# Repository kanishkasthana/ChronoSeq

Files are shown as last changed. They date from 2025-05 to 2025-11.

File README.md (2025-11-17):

# Software and Protocols for [ChronoSeq](https://github.com/kanishkasthana/ChronoSeq)

### [Project Map](https://kanishkasthana.github.io/ChronoSeq/sitemap.html)
+ First time users should visit [this website](https://kanishkasthana.github.io/ChronoSeq/sitemap.html) first as it provides an overview of the ChronoSeq project. You can click on and directly go the the relevant information. There are two main notebooks for Device assembly and Device operation as linked below. These notebooks should have the links to help you follow the correct instructions in the right order. Please read the disclaimer below before starting. 

### Getting Started with Software 
+ Install [Git X86-64-Bit for Windows](https://git-scm.com/download/win) and [Anaconda X86-64-Bit for Windows](https://www.anaconda.com/download), on your [Windows X86-64 Bit PC](Computer%20Selection.md).
+ Type "Git Bash" in the Search bar next to the Start Button. Using Git Bash clone this repository.
    + Using Git Bash [Navigate to the directory](https://tutorials.codebar.io/command-line/introduction/tutorial.html) where you want to store this repository.
    + This repository has submodules. In Git Bash, use the command ```> git clone --recursive https://github.com/kanishkasthana/ChronoSeq.git```  when cloning this repository so the submodules are also cloned.
+ Type "Anaconda Prompt" in the Search bar next to the Start Button. Now create a [new environment](https://conda.io/projects/conda/en/latest/user-guide/tasks/manage-environments.html#creating-an-environment-from-an-environment-yml-file) called Chrono from [this file](conda_environment_file/chrono.env.yml)
+ [Activate the Environment](https://docs.conda.io/projects/conda/en/latest/user-guide/tasks/manage-environments.html#activating-an-environment) from the Anaconda Prompt. 
+ Using the Anaconda Prompt navigate to the directory for the git repository you cloned.
    + Alternatively you can modify your Anaconda Prompt shortcut so that it always activates the Chrono Environment and launches at the location of your Git repository. I've included [an example here](conda_environment_file/Anaconda%20Prompt.lnk).
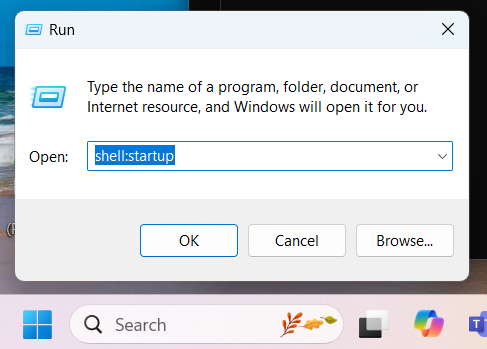
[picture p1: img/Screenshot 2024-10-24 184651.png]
    + Open Run and type ```shell:startup``` to open your startup folder.<br>
    + You can copy the shortcut included to this startup folder.
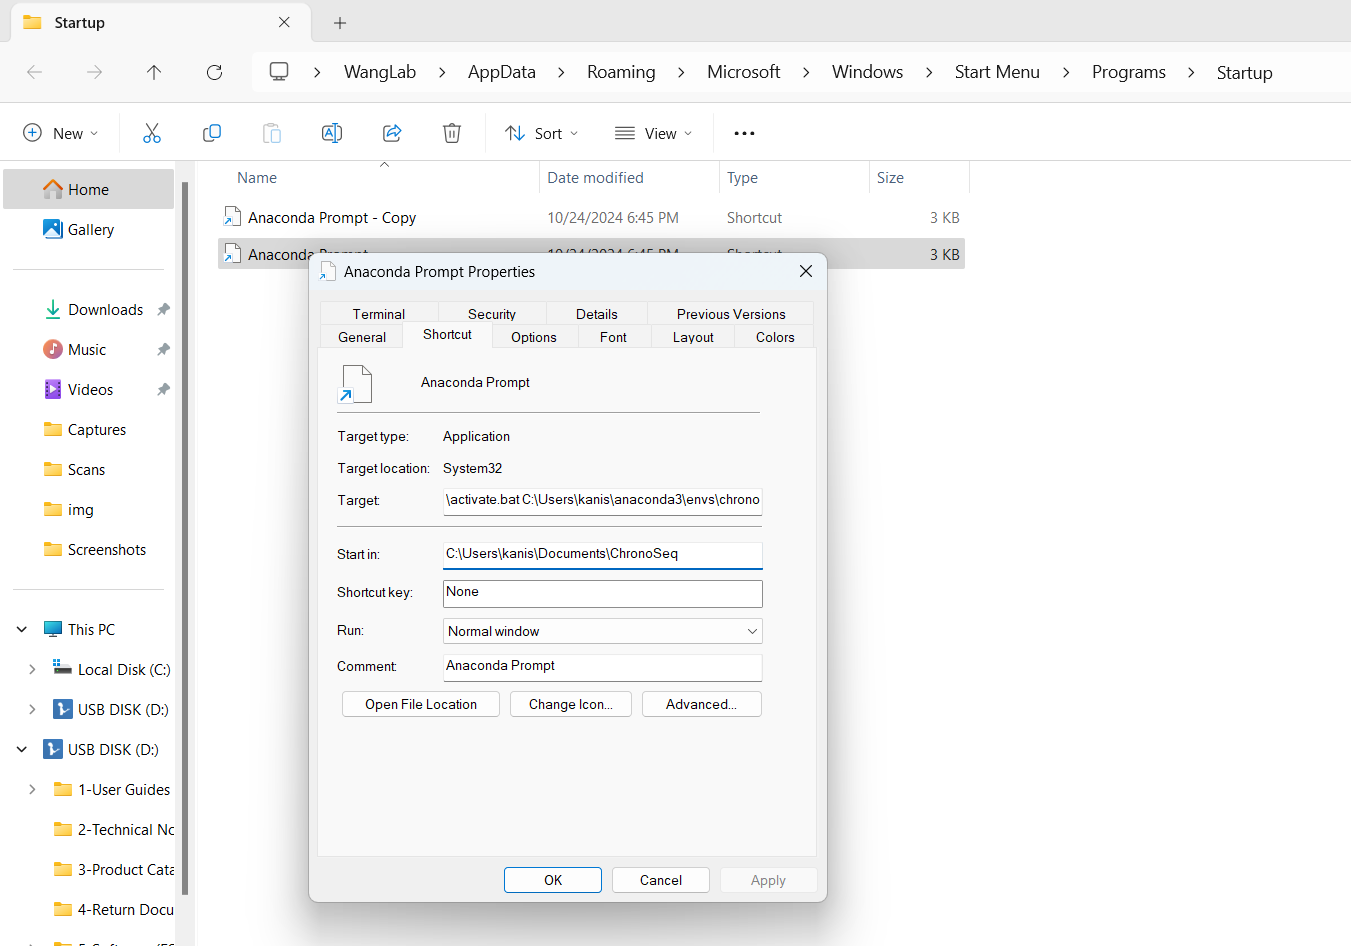
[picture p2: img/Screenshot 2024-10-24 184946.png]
    + Then right click the shortcut and change the ```Target``` and ```Start In``` sections so that a command line terminal with the environment automatically activated opens during startup.<br>
+ Using Anaconda Prompt Run ```> jupyter notebook``` 
+ The links to the notebooks below are intended to be opened using Jupyter. Click the image below to watch a video of the process.
<br>[](https://www.youtube.com/watch?v=qbhCONpUdx0)

### Device Assembly
+ See the [Device Assembly and Setup notebook](instructions_for_device_assembly_and_setup.ipynb) for a detailed description of how to set everything up.

### Storage of Dropseq beads upon receipt
+ You should receive your beads suspended in Ethanol.
+ Store these beads in a new box at -20&deg;C before you start your experiments or for long term storage. Label the box with the Date you received the beads, the bead type and the batch number.

### Running the Device and Preparation for Experiment
+ Once you are ready, see [this notebook](protocol_and_software_for_running_chronoseq_device.ipynb#Protocol-for-Preparation-and-Operation-of-the-ChronoSeq-Device-for-an-Experiment.) on how to run the Device and the preparation needed.

### Videos of Device Operation
+ Click the image below to watch a video of the view from inside the microfluidic chip during an Injection.<br>[](https://www.youtube.com/watch?v=J2O1kA4chU0)
+ Click the image below to watch an outside view of the ChronoSeq device during an Injection. <br>[](https://www.youtube.com/watch?v=qFouf2HrKSk)

### Build Compilation Music Video
+ Click the image below to watch a music video of the iteration/build process for making the ChronoSeq device.<br>[](https://www.youtube.com/watch?v=QpMUR4AgpgA)

# License

We have released this work under a [CC BY-NC-SA 4.0 License](LICENSE).

# Disclaimer

Dear Fellow Users and Researchers,
<br><br>
We are thrilled that you are interested in assembling the ChronoSeq Device we have created. However, it is important to note that we cannot be held responsible for any injuries that may occur during the assembly and operation process.<br>
While we strive to provide clear and concise instructions, the assembly of this open source hardware requires a certain level of skill and experience. Therefore, we strongly recommend that you take all necessary precautions to ensure your safety.<br>
Please read and follow all instructions carefully, and make sure that you have the necessary tools and protective equipment. If you are unsure about any step or procedure, do not hesitate to seek the advice of a qualified professional. You are also welcome to raise [an issue](https://github.com/kanishkasthana/ChronoSeq/issues) or [start a discussion](https://github.com/kanishkasthana/ChronoSeq/discussions) if you have any questions or if anything is unclear.<br> 
<br>
By using or constructing this open source hardware design, you acknowledge and agree to the following:
1. Liability Waiver: The creators, designers, and contributors of this open source hardware project cannot be held liable for any injuries, damages, or losses resulting from the use, construction, or modification of this hardware.
2. Assumption of Risk: You, as the builder or user, assume all risks associated with the construction, use, and modification of this hardware. This includes, but is not limited to, personal injury, property damage, or any other potential harm.
3. Waiver of Legal Action: By proceeding with the use or construction of this open source hardware, you waive your right to sue, hold legally responsible, or seek compensation from the creators, designers, or contributors for any reason related to this project.
4. No Warranty: This open source hardware is provided "as is" without any express or implied warranties. The creators make no guarantees regarding its safety, functionality, or fitness for any particular purpose.
5. Responsibility: You are solely responsible for ensuring that you follow all safety precautions, local laws, and regulations when building or using this hardware.
6. Modifications: Any modifications you make to the original design are your sole responsibility, and the original creators bear no liability for the results of such modifications.
<br>By proceeding with the use or construction of this open source hardware, you indicate your understanding and acceptance of these terms.

Thank you for choosing our open source hardware, and we hope that you enjoy the building and operation process.
<br><br>
Best regards,
<br>ChronoSeq Team:
<br>Kanishk Asthana [kasthana@ucsd.edu](mailto:kasthana@ucsd.edu) , [X/Twitter](https://x.com/kanishk_asthana)
<br>Alexander Jambor [ajambor@ucsd.edu](mailto:ajambor@ucsd.edu)
<br>Wei Wang [wei-wang@ucsd.edu](mailto:wei-wang@ucsd.edu)

# Data Processing and Analysis

+ Check out the [ChronoSeq-Tools repo](https://github.com/kanishkasthana/ChronoSeq-Tools) to help process your raw data.
+ Check out the [ChronoSeq-QC repo](https://github.com/kanishkasthana/ChronoSeq-QC) to see how the QC plots were generated.
+ Check out the [ChronoPack repo](https://github.com/anjambor/ChronoPack) to see how the ChronoSeq data was analysed.

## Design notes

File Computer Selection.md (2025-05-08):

### We purchased the [Dell Inspiron Small Desktop](https://www.dell.com/en-us/shop/desktop-computers/inspiron-small-desktop/spd/inspiron-3030-small-desktop/useishbts3030gssh). 
+ Please purchase a Computer with the same Tech Specs or better.
+ Make sure there are at least four USB 3.2 Gen 1 Ports on your machine.
+ We used an [adapter to convert one of the USB 3.2 Gen 1 Type C ports to a Type A port](https://www.amazon.com/dp/B0CNK3YK1J).
+ The price was 600 USD before taxes and shipping in October 2024.

### Tech Specs:

+ Processor:
    + Intel® Core™ i5 14400 (20 MB cache, 10 Cores, 16 threads, up to 4.7 GHz)
+ Operating System
    + Windows 11 Home, English, French, Spanish
+ Graphics Card
    + Intel® UHD Graphics 730
+ Memory 
    + 16GB DDR5, 1x16GB, at 4400 MT/s
+ Storage
    + 512GB M.2 PCIe NVMe Solid State Drive
+ Ports
    + Front:
        + 2 USB 2.0 Type-A ports
        + 1 USB 3.2 Type-A Gen 1 port
        + 1 USB 3.2 Type-C Gen 1 port
        + 1 Universal headset jack
    + Rear:
        + 2 USB 2.0 Type-A ports with Power on/Wake support
        + 2 USB 3.2 Type-A Gen 1 port
        + 1 Audio line-out port
        + 1 DisplayPort 1.4 port
        + 1 RJ-45 Ethernet port
        + 1 HDMI 1.4b port <br> Note: The maximum resolution supported by HDMI 1.4b port is 1920 x 1200.
+ Dimensions
    + Height (rear): 11.42 in. (290.00 mm)
    + Height (front): 11.42 in. (290.00 mm)
    + Width: 3.65 in. (92.60 mm)
    + Depth: 11.53 in. (292.80 mm)
+ Wireless 
    + Realtek Wi-Fi 6 RTL8852BE, 2x2, 802.11ax, MU-MIMO, Bluetooth® wireless card

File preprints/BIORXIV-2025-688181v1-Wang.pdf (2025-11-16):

Minute-scale single-cell transcriptomics enables dynamic modeling of cellular behavior

Kanishk Asthana†‡,1,2, Alexander N. Jambor†,1,2, and Wei Wang‡,1,2,3,4

1 Department of Chemistry and Biochemistry, University of California San Diego, La Jolla, CA 92093, USA
2 Bioinformatics and Systems Biology PhD Program, University of California San Diego, La Jolla, CA 92093, USA 3 Department of Cellular and Molecular Medicine, University of California San Diego, La Jolla, CA 92093, USA
4 Lead contact
† Equal contribution
‡ Corresponding authors

Corresponding author contact information: Kanishk Asthana: kasthana@ucsd.edu Wei Wang: wei-wang@ucsd.edu

Abstract

Dynamic cellular processes such as signaling, fate decisions, and intercellular communication unfold on minute timescales, a regime inaccessible to conventional transcriptomic methods. This temporal gap has fundamentally limited the development of predictive, causal models of cell behavior. Here, we bridge this gap by introducing ChronoSeq, an automated single-cell RNA sequencing platform that achieves genome-wide profiling with a temporal resolution as brief as seven minutes. By integrating automated live-cell sampling with molecular time-barcoding, ChronoSeq captures rapid transcriptional dynamics with high fidelity. Applying ChronoSeq to TNF-α stimulated cells, we discovered a rapid, heterogeneity-driven bifurcation in the NF-κB response that was previously unobservable. We further demonstrate that the highdensity temporal data generated by ChronoSeq enables a new class of computational models that dramatically outperform existing methods in inferring the directionality and targets of post-translationally regulated transcription factors. Finally, in a multicellular co-culture, ChronoSeq resolved a paracrine signaling cascade in real time, identifying both the timing and molecular identity of the intercellular relay. By providing a framework to measure dynamics, infer regulation, and model communication at the true pace of biology, ChronoSeq establishes a new foundation for dynamic systems biology.

Introduction
Building predictive, dynamic models of cellular behavior, the vision of a “Virtual Cell”¹,2, requires experimental data that reveal how gene regulation and cell-cell communication unfold in real time. Achieving this vision depends on three core capabilities: capturing transcriptional dynamics on the natural timescales of signaling and fate decisions, inferring causal rather than correlative gene regulatory networks (GRNs), and resolving the timing of multicellular communication that coordinates collective responses. Yet current methodological and data limitations have kept these goals largely out of reach.

Many cellular processes operate on minute timescales³⁻⁵
, a regime inaccessible to standard single-cell RNA sequencing (scRNAseq)⁶⁻¹⁶ . For example, the NF-κB signaling cascade activates transcriptional responses within 5 minutes of TNF-α stimulation and peaks at around 25 minutes¹⁷, timescales that are effectively invisible at the 30–60 minute resolution of existing scRNA-seq. Without dense, accurately timed expression measurements, computational efforts to infer causality or simulate cellular decision-making remain fundamentally constrained.

Several specialized methods have attempted to address this gap, but each fall short of combining fidelity, temporal resolution, and throughput. Metabolic labeling¹⁸⁻²³ and scGROseq²⁴ can detect nascent transcripts yet suffer from manual processing errors and low scalability. Liveseq⁶ preserves cell viability but has hourly sampling intervals and limited throughput. Live-cell imaging²⁵⁻²⁷ captures real-time trajectories only for a few marker genes and is hindered by phototoxicity and narrow genomic coverage²⁸. No current technology achieves genome-wide, minute-scale measurements under physiological conditions with full experimental automation, capabilities that are essential for generating the benchmark datasets required for dynamic in silico modeling.

To bridge this gap, we introduce ChronoSeq, an automated droplet-based single-cell RNA sequencing platform that performs genome-wide profiling with a sampling interval as brief as seven minutes. ChronoSeq integrates automated sampling with molecular time-barcoding into a single workflow, preserving cell health while capturing transcriptional dynamics over extended perturbations. Together with a companion computational suite, ChronoPack, this technology provides an integrated framework to measure dynamics, infer causality, and model intercellular communication, the core components of Virtual Cell.

We demonstrate these capabilities through proof-of-concept studies addressing rapid signaling, causal inference, and multicellular communication. Minute-scale profiling of TNF-α stimulated K562 cells revealed a rapid bifurcation into erythroid and non-erythroid trajectories, directly capturing fate transitions as they occurred. Using ChronoPack, we reconstructed temporally informed GRNs that outperformed existing inference methods, yielding mechanistic insight into early transcriptional regulation. Finally, in a co-culture of THP1 macrophages and K562 cells, ChronoSeq resolved secondary paracrine signaling induced by the LPS stimulation of THP1 cells, pinpointing the timing and molecular identity of secreted factors mediating cross-cell activation.

By combining genome-wide, minute-scale temporal profiling with causal network inference and intercellular dynamics, ChronoSeq establishes a new foundation for dynamic systems biology. This integration brings the Virtual Cell concept within reach, linking molecular mechanism to phenotype in predictive, quantitative terms.

Results
An automated platform for minute-scale temporal scRNA-seq
To directly observe rapid transcriptional dynamics, we developed ChronoSeq, an automated platform that integrates live-cell culture with droplet-based scRNA-seq. The system performs programmed sampling at intervals as short as seven minutes, co-encapsulating each cell with uniquely barcoded Time-Tag beads (Fig. 1a, Fig. S2, Supplementary Movie 1). Immediate lysis upon droplet formation preserves the transcriptional state, while all timepoints are processed within a single library to dramatically reduce labor while eliminating batch effects and manual variability (Fig. S1). Continuous cell maintenance under physiological conditions ensures that captured profiles reflect authentic biological responses.

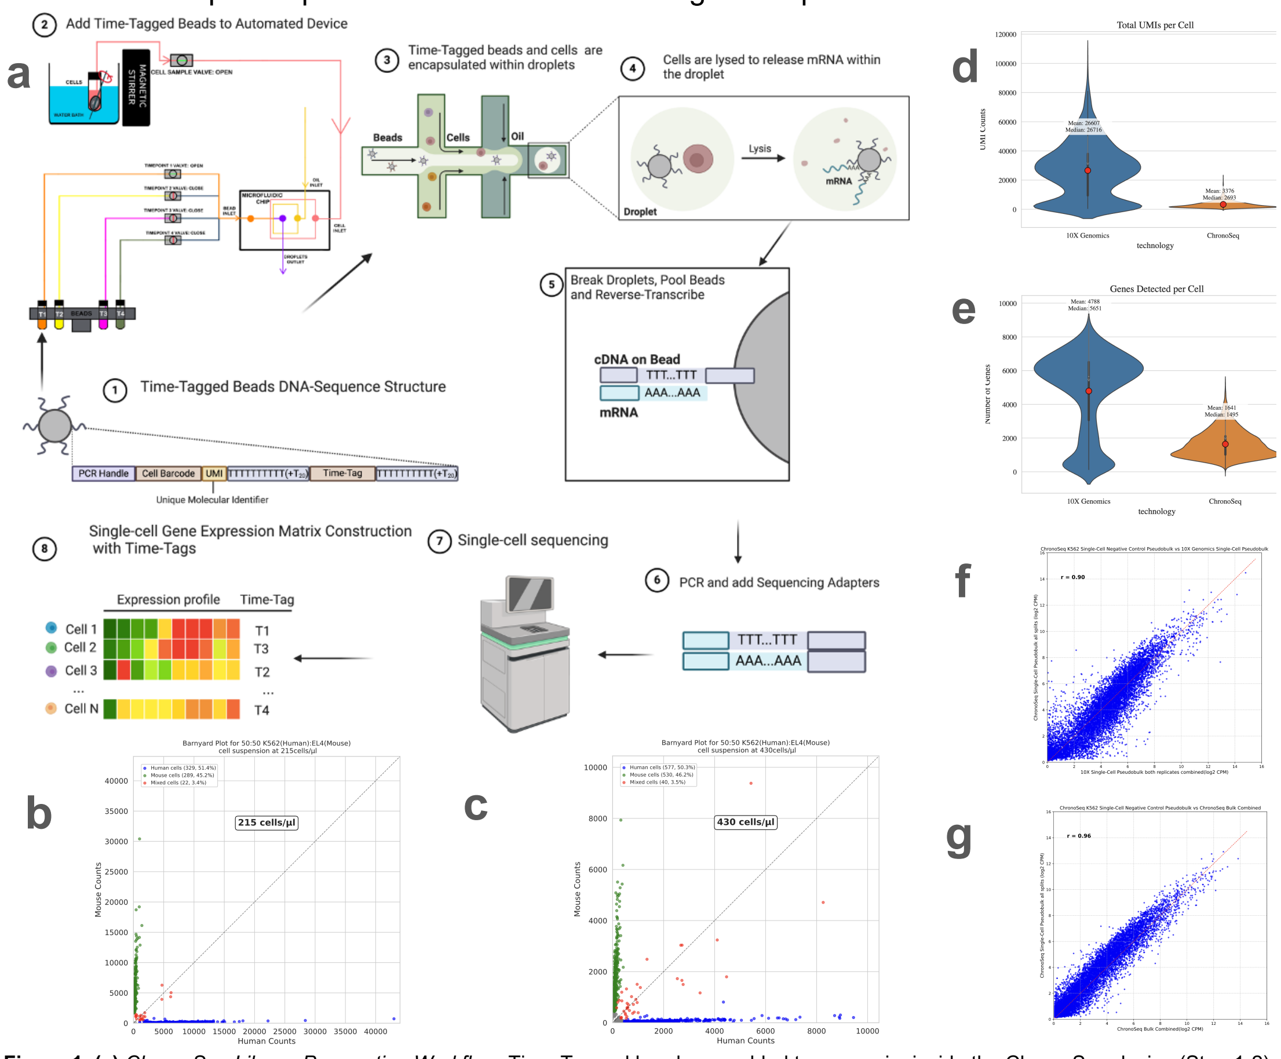
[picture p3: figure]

Figure 1. (a) ChronoSeq Library Preparation Workflow: Time-Tagged beads are added to reservoirs inside the ChronoSeq device (Step 1-2). Our current system supports 12 unique Time-Tags, each Time-Tag is added to its own dedicated reservoir. Cells suspended in a culture media are loaded into another reservoir maintained at 37°C and 5%CO2. The ChronoSeq device then automatically co-injects Time-Tags 1-12 with samples 1-12 from the Cell reservoir into a microfluidic chip at programmed time intervals of 7 minutes or longer (Supplementary Movie 1 and Figure S2). This results in droplets where cells collected from each sample 1-12 are present with ChronoSeq beads with the same Time-Tags 1-12 (Step 3). Cells are immediately lysed upon droplet formation and kept on ice to preserve the transcriptome until all 12 samples are collected (Step 4). For samples with high RNAase activity, RNAase inhibitor is added to each sample to help further maintain RNA integrity. Next, following the same process as Drop-seq, droplets are broken, pooled, and reverse transcribed together in unified library preparation workflow for all samples. The cDNA on the beads is amplified and sequencing adapters are added (Steps 5-6). The library is sequenced and processed with our ChronoSeq-Tools pipeline to create Digital Gene Express Matrices (DGEs) with a Time-Tag number for each cell (Steps 7-8). (b,c) Species-mixing barnyard plots for 50:50 K562(Human) and EL4(Mouse) cells at two commonly used ChronoSeq working concentrations (215 cells/ul and 430 cells/ul). (d-g) We generated K562 negative control datasets using both single-cell and bulk sampling using the ChronoSeq device. For both bulk and single-cell datasets, K562 cells were maintained inside the ChronoSeq device and samples were taken using the ChronoSeq device at programmed intervals of 10 minutes. For the bulk dataset, cells sampled by the device

We manufactured (Fig. S3) and validated the fidelity of the 12-plex Time-Tag barcode system using mixed human–mouse samples. Each tag cleanly partitioned species-specific transcripts, with minimal barcode cross-talk (<=1.6% mixed beads per tag; Fig. S4). Automated sampling within the ChronoSeq device showed similarly precise tagging and each cell population was exclusively labeled with its designated barcode (Fig. S5). ChronoSeq’s single-cell capture efficiency matched commercial standards, with a doublet rate below 4% across operational cell concentrations (Fig. 1b,c). We captured an average of 636 cells per Time-Tag. Together, these results demonstrate that ChronoSeq achieves fully automated, high-integrity sample tagging and single-cell encapsulation.

To benchmark transcriptional accuracy independently of temporal resolution, we profiled unstimulated K562 cells using ChronoSeq. Despite the number of detected genes and transcripts per cell being lower than 10X Chromium (Fig. 1d,e), ChronoSeq exhibited quantitative fidelity: pseudobulk profiles from ChronoSeq single cells correlated nearly perfectly with ChronoSeq bulk RNA-seq (r = 0.96) and strongly with 10x Chromium pseudobulks (r =
0.90) (Fig. 1f,g). These results confirm that ChronoSeq accurately preserves transcriptional signatures, with minimal bias introduced by automated sampling. The high concordance establishes a robust foundation for interpreting minute-scale biological dynamics.

ChronoSeq reveals rapid fate bifurcation during the NF-κB inflammatory response
To demonstrate ChronoSeq’s ability to resolve rapid transcriptional dynamics, we profiled K562 cells responding to TNF-α stimulation at 10-minute intervals over 2 hours, which is known to activate the NF-κB pathway. Temporal pseudobulk profiles showed high concordance with matched qPCR timecourses for representative NF-κB target genes (Fig. S6), validating ChronoSeq’s ability to capture real-time dynamics.

We developed ChronoPack, an open-source computational suite for quantitative analysis of time-resolved single-cell data (Fig. 2a). The suite integrates standard preprocessing, expression correction, and metacell construction, followed by trajectory inference using WaddingtonOT³⁰ to derive a probabilistic cell-state transition kernel across time. This kernel enables cell-fate mapping, dynamic clustering, and the identification of early predictive genes. Temporal gene expression is modeled with negative-binomial generalized additive models (NB-GAMs) using tradeSeq³¹ to detect statistically significant expression trends. Building on these results, ChronoPack can also infer causal gene regulatory networks from time-resolved dynamics and reconstruct paracrine signaling by integrating ligand–receptor databases with Granger causality analysis. Collectively, ChronoPack provides a unified framework for inferring causal regulation and intercellular communication from high-temporal-resolution scRNA-seq data.

Trajectory reconstruction using ChronoPack revealed a striking, previously uncharacterized bifurcation in the NF-κB response emerging within minutes of stimulation (Fig. 2a,e). One subpopulation activates the classical inflammatory program, marked by strong induction of NF-κB hallmark genes like NFKBIA and ICAM1, whereas a smaller, erythroid-like subpopulation responds weakly (Fig. 2c,d). This rapid divergence indicates that intrinsic cell-state

were manually mixed with Time-Tags 1-12. d-e) We downloaded both replicates of a published K562 dataset²⁹ generated using the commercially available 10X Genomics Chromium 3’ single-cell RNA-seq technology for comparison: (d) shows a violin plot comparing mean and median transcripts captured, (e) shows a violin plot comparing genes detected for the 10X Genomics dataset and ChronoSeq single-cell K562 negative control dataset. (f-g) We prepared pseudobulks across all Time-Tags for both bulk and single-cell ChronoSeq K562 negative control datasets. We also prepared a combined pseudobulk for both 10X Genomics K562 replicates. (f) shows a correlation scatterplot between the 10X Genomics and ChronoSeq single-cell K562 pseudobulks. ChronoSeq shows a high concordance with 10X Genomics with a correlation coefficient r=0.90. (g) Comparison of ChronoSeq single-cell and bulk shows even higher concordance with a correlation coefficient r=0.96.

heterogeneity preconfigures responsiveness to inflammatory signaling, influencing both the timing and magnitude of NF-κB activation.

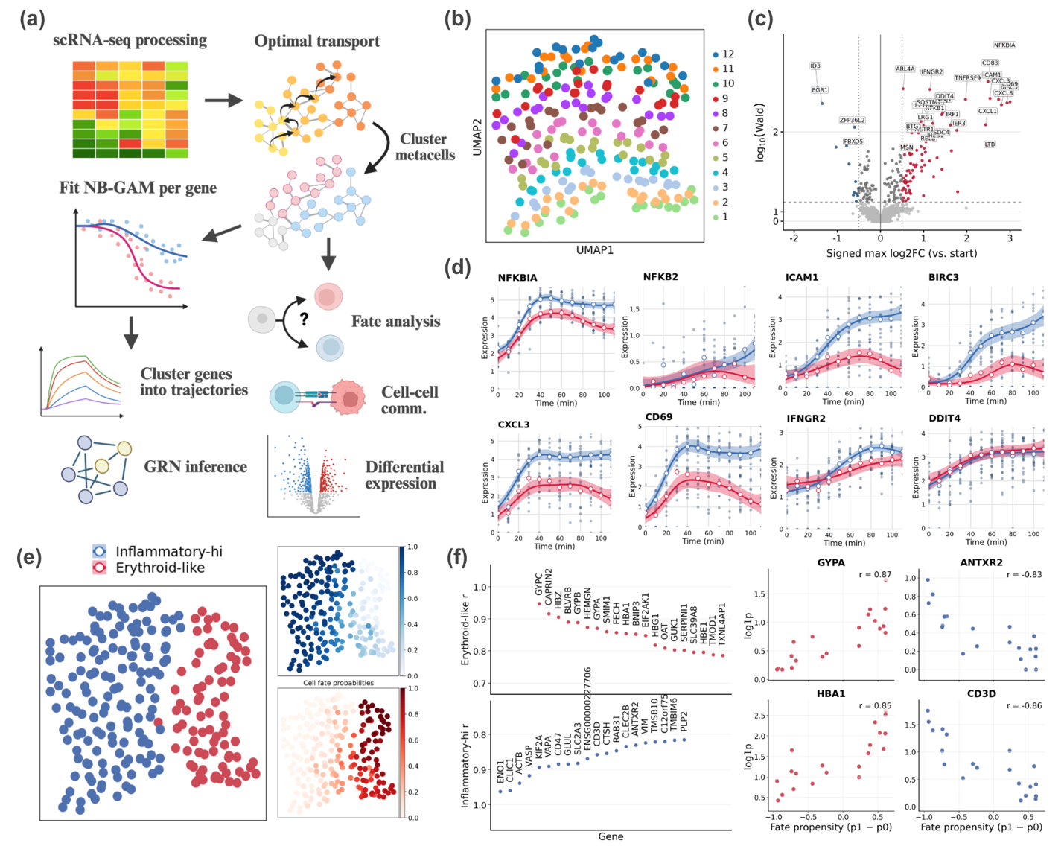
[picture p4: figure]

We next quantified gene-specific dynamics along each trajectory using negative-binomial generalized additive models (NB-GAMs). After filtering for genes with Time-Tag-specific capture biases, we identified 184 high-confidence temporally regulated genes, including both upregulated and a few immediate-early genes like ID3 and EGR1 which decreased in expression over time (Fig. 2c). The representative trajectories in Fig. 2d highlight the underlying biology: canonical NF-κB targets (e.g., NFKBIA, NFKB2, ICAM1, BIRC3, CXCL3) rise rapidly in the inflammatory trajectory but are dampened in the erythroid-like K562 cells, which express HBE1, HBA2, GYPC, and other lineage markers. These results indicate that pre-existing

Figure 2. (a) Overview of ChronoPack package workflow. ChronoPack is an integrated computational package for time-resolved single-cell analysis. It performs standard preprocessing, expression correction, and metacell construction, followed by trajectory inference using WaddingtonOT-derived transition kernels. The suite quantifies temporal gene trends with negative-binomial generalized additive models (NB-GAMs), reconstructs causal gene regulatory networks, and infers dynamic cell–cell communication through time-lagged ligand–receptor analysis. Together, these modules enable end-to-end analysis of ChronoSeq datasets from raw counts to causal dynamics. (b) UMAP of K562 scRNA-seq time series experiment based on derived transition kernel. (c) Volcano plot of highly varying genes depicting temporal trend scores (i.e., log10(Wg)) vs. maximum log2FC, where Wg is the Wald test statistic from tradeSeq's associationTest. Genes are labeled as significantly trending over time if q<0.01 at an FDR of 0.05 (calculated by applying Benjamini-Hochberg to the p-values associated with Wg), and as upregulated or downregulated based on whether abs(log2FC) exceeds 0.5. Here, abs(log2FC) is taken to be the highest log-fold change observed across time points vs. t=0. (d) Gene trajectories for representative genes highlight the differential NF-kB response across K562 erythroid identity. (e) Metacell fate probabilities for the two response types based on the WaddingtonOT³⁰-derived transition kernel. Terminal fates are identified as the last measured metacells in either response. (f) (left) Top 20 genes whose expression in early metacells correlated with fate propensity. (right) Expression vs. fate propensity plots for representative genes.

erythroid identity constrains the amplitude and persistence of the NF-κB transcriptional response.

Finally, to identify genes associated with the differential NF-κB response, we designated the terminal metacells in each trajectory as distinct fates and calculated fate probabilities using the transition kernel. Since this kernel forms a directed acyclic graph, we computed fate probabilities by dynamic programming, first assigning probabilities to terminal cells and then recursively back-propagating these values to progressively earlier cells along the graph. Correlating gene expression with these probabilities revealed a set of early markers predictive of fate choice (Fig. 2e-f). Genes enriched in the inflammatory trajectory included immune and myeloid-like regulators such as KLF2A and CD3D, whereas the alternative trajectory was characterized by erythroid-associated genes like HBA1 and GYPA. These findings not only validate the observed phenotypic bifurcation but also identify potential regulators that may instruct this cell fate decision.

Minute-scale temporal data enables causal inference of gene regulation
We next investigated whether ChronoSeq’s dense temporal sampling could improve causal inference of gene regulatory networks (GRNs). The TNF-α stimulation of K562 cells kickstarts an intracellular signaling cascade that culminates in the rapid nuclear translocation of NF-κB (NFKB1-RELA) and the activation of AP-1 via MAPK signaling³². Traditional co-expression methods struggle to model transcription factors (TFs) with post-translational activity changes, such as RELA/p65 whose mRNA level remains stable during the NF-κB response. As part of the ChronoPack analysis suite, we have developed an inference strategy for application to rapid signaling contexts like NF-κB (Fig. 3a), in which the stimulus is conceptualized as an intervention impacting the activity of several unknown TFs. Our motivating hypothesis is that genes with significant temporal changes are enriched for direct targets of TFs whose activity shifts downstream of the stimulus. Following this logic, GRN inference proceeds by first (i) prioritizing TFs according to their downstream proximity to the stimulus, leveraging OmniPath³³ protein–protein interaction and pathway annotations to identify the TFs most likely to undergo activity changes, and (ii) ranking potential target genes according to the significance of their temporal expression dynamics. The resulting TF ranking captures both epistemic uncertainty about which TFs are perturbed as well as genuine biological multiplicity where several TFs may be affected by the same stimulus. TF and gene rankings are then combined additively to construct an edge list for network prediction, with a substantial rank penalty applied to edges terminating at genes without significant temporal trends (i.e., q > 0.01).

When benchmarked against four state-of-the-art algorithms (GENIE3, GRNBoost2, SINCERITIES, and PPCOR)³⁴⁻³⁷, ChronoPack achieved the highest early precision (EPr) and area under the precision–recall curve (AUPRCr) ratios across relevant TFs, including the NF-κB axis (e.g., NFKB1/RELA) and immediate-early AP-1 factors (FOS/JUN). Against curated human TRRUST interactions, ChronoPack demonstrates a nearly 3-fold improvement in mean performance over the best co-expression-based method, GRNBoost2 (Fig. 3b; EPr: 6.7 vs. 2.3, AUPRCr: 7.0 vs. 2.5). These predictions were independently supported by two K562-specific ChIP-seq networks derived from ENCODE³⁸ and taken from CausalBench³⁹. Compared to TRRUST⁴⁰, ChIP-seq-derived ground-truth networks, although data-driven and cell typespecific, are constrained by their strong context dependence and by the fact that physical TF-DNA binding does not necessarily equate to functional regulation. However, despite their lower specificity for true NF-κB regulation, we observed a consistent gain in EPr and AUPRCr on both ChIP-seq-based benchmarks. Interestingly, this improvement generalized to several TFs not expected to be differentially activated by TNF-α stimulation. This likely reflects the fact that the regulons of these TFs are enriched for immediate early and stress-responsive genes. Erythroiddriving TFs like GATA1 and TAL1 also exhibited higher predictive performance, possibly due to overlap in their downstream targets with the NF-κB transcriptional program.

Per-TF performance makes the contrast between ChronoPack and co-expression baselines especially clear. For RELA (p65), ChronoPack outperforms other methods by a wide margin (Fig. 3c; AUPRCr: 7.8 vs. 1.8 @ GRNBoost2), because RELA's activity after TNF-α is driven by rapid post-translational control rather than a change in mRNA abundance – leaving co-expression methods with little signal to exploit. ChronoPack maintains high early precision (~0.30) by identifying perturbed TFs and prioritizing targets with clear temporal trends, whereas other methods are only marginally better than a random predictor. For NFKB1, the gap narrows (AUPRCr: 7.2 vs. 5.8 @ GRNBoost2) largely because NFKB1 is itself an NF-κB-inducible gene, resulting in apparent co-expression with true regulatory targets. Collectively, these findings demonstrate that high-temporal-resolution single-cell data from ChronoSeq improve the reconstruction of gene regulatory networks, revealing transcriptional control relationships that remain obscured in static datasets.

To distinguish direct TF-gene interactions from indirect responses, we repeated the TNF-α stimulation of K562 cells in the presence of puromycin, which blocks translation (Fig. 3d). Under this co-treatment, pre-existing NF-κB TFs can still translocate to the nucleus and bind DNA, but de novo synthesis of downstream transcriptional regulators and feedback inhibitors is largely prevented. Genes whose temporal trajectories are preserved in the presence of puromycin are therefore expected to be directly driven by stimulus-responsive TFs, whereas attenuated responses indicate dependence on newly translated intermediates. Consistent with this model, canonical NF-κB targets including NFKBIA, CXCL1, ICAM1, TNFRSF9, and IRF1, as well as NFKB1 itself, show robust, and in many cases augmented, induction with puromycin co-treatment – likely reflecting the loss of translationally-dependent negative feedback (e.g., reduced synthesis of IκBα and other inhibitors). These results provide functional support that ChronoPack-predicted regulatory edges, and more broadly, genes with significant temporal trends apparent within the first two hours of response, correspond predominantly to direct regulatory interactions.

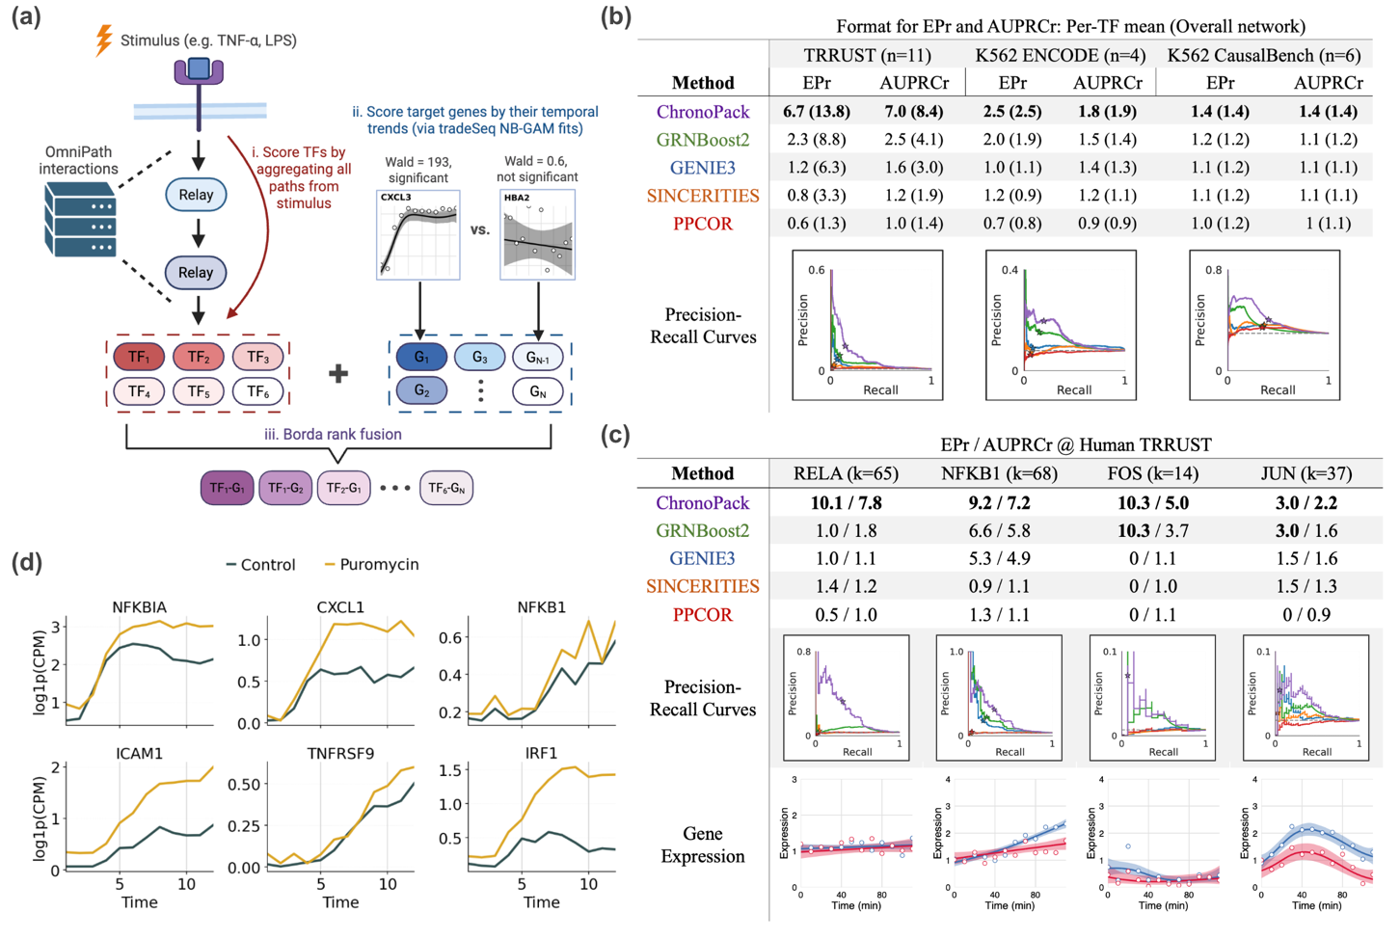
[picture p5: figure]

ChronoSeq recovers a paracrine TNF signaling cascade during multicellular immune activation
To test whether ChronoSeq can resolve dynamic cell-cell communication, we modeled innate immune secondary signaling via an interaction between LPS-responsive THP-1 macrophages and LPS-unresponsive K562 cells (Fig. S7). Following LPS stimulation, high-temporalresolution profiling at 15-minute intervals revealed a sequential transcriptional response: THP-1 cells rapidly initiated a canonical inflammatory program, while K562 cells displayed a delayed, secondary response dependent on THP-1 co-culture (Fig. 4a,b). Two key features emerged: (i) a ~45 min lag in K562 activation relative to THP1, and (ii) the presence of cell type–specific gene programs. Differential temporal association and log₂ fold-change contrasts between THP1 and K562 (Fig. 4c) revealed an LPS/TLR4-biased module (e.g., TNFAIP2, TNFAIP3, NFKBIZ, CCL3, CCL4) versus a TNF-specific program (CD69, IRF1, LTB). These differences underscore the functional distinction between LPS-induced and paracrine TNF-α-induced NF-kB inflammatory responses in THP1 and K562, respectively. A subset of chemokines (CXCL1, CXCL3, CXCL8) were preferentially but not exclusively expressed in THP1 cells.

This experimental design allows us to prioritize ligand-receptor pairs which precede and are predictive of the K562 response. As seen from Fig. 4b, TNF expression rises early in THP1 and precedes the K562 NF-κB response by approximately 45 minutes (Fig. 4e). The temporal

Figure 3. (a) Overview of ChronoPack GRN inference methodology. (b) Early precision (EPr) and area-under-precision-recall-curve ratios (AUPRCr) across inference methods and benchmark datasets (Human TRRUST⁴⁰ regulatory edges and two ChIP-seq-derived networks using either (i) K562 ChIP-seq experiments from ENCODE³⁸ or (ii) CausalBench's³⁹ K562 ground-truth). n = the number of NF-κB-relevant TFs evaluated and present in the ground-truth network. Reported metrics are formatted as per-TF mean (overall network), where the latter indicates performance for the entire subnetwork spanned by the NF-κB TFs. (c) Inference performance for individual NF-κB TFs. k = number of gene targets evaluated for the TF. (d) Mean expression curves for select NF-κB hallmark genes following TNF-α stimulation with and without puromycin addition. Lack of response attenuation with puromycin implies direct regulation.

ordering, specificity, and known TNF biology support a paracrine TNF relay from THP1 cells that drives the delayed K562 response⁴¹⁻⁴³ To quantitatively identify candidate mediators of the delayed K562 activation, we used CellChatDB⁴⁴ annotations to compute ligand–receptor (L–R) activity scores (ligand in THP1, receptor in K562) over time and applied an autoregressive with exogenous input (ARX)/Granger causality⁴⁵ to screen L–R pairs against the K562 NF-κB response (Fig. 4d). Specifically, we tested whether the activity time series for a given L-R activity pair Granger-caused K562's NF-κB response across a plausible set of lags (between 30-75 min). This analysis prioritized pairs whose activity preceded and predicted K562 activation, where TNF–TNFRSF1A and TNF–TNFRSF1B emerged as top candidates. Consistent with this, TNF transcripts sharply increased in THP-1 cells within minutes of LPS exposure, preceding the late induction of NF-κB target genes such as ICAM1 and NFKBIA in K562 cells. These results demonstrate that ChronoSeq can temporally resolve and causally attribute multicellular signaling events, providing a direct systems-level view of how paracrine communication unfolds in real time.

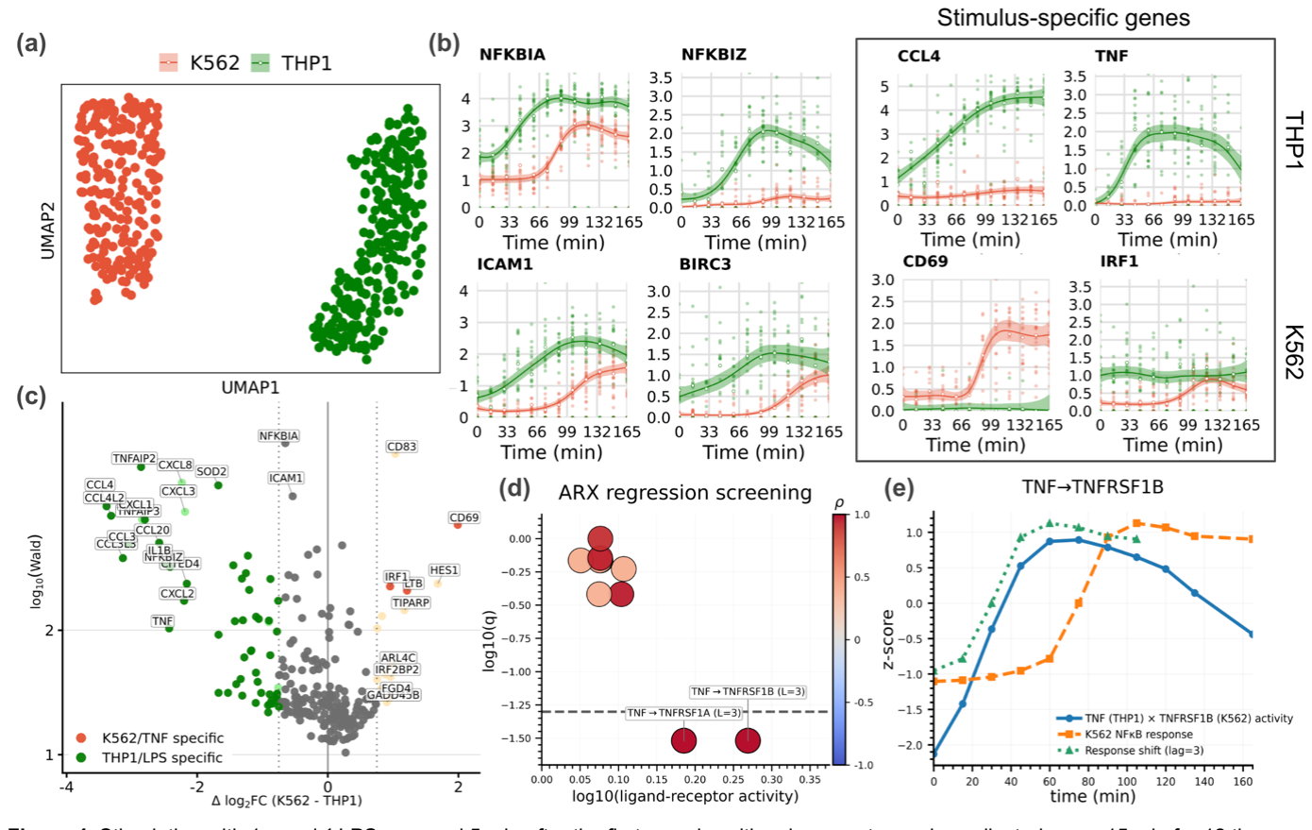
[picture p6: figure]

Figure 4. Stimulation with 1 μg ml⁻¹ LPS occurred 5 min after the first sample, with subsequent samples collected every 15 min for 12 time points. At this LPS concentration, THP1 cells respond via TLR4 signaling⁴⁶,47, whereas K562 cells remain unresponsive (Fig S7). (a) UMAP visualization of THP1 and K562 cells. (b) Gene expression trajectories for select genes demonstrating a lagged NF-kB response and stimulusspecific genes. (c) Volcano plot of significantly trending genes vs. their difference in maximum log2FC across the two cell lines. Darker colors are used to highlight genes with log2FC < 0.5 in the other cell/stimulus type, indicating specificity. (d) Granger-style regression screening of ligand-receptor candidates. (e) Visualization of TNF-TNFRSF1B ligand-receptor activity vs. K562 NF-kB response

Discussion
We have demonstrated that ChronoSeq addresses a practical bottleneck in time-resolved single-cell transcriptomics. By automating sample collection across time points and consolidating them into a single library via time-barcoded beads, ChronoSeq achieves minute-level sampling of expression dynamics over multiple hours. Automation and the immediate cell lysis help eliminate human errors in sampling and labelling, while integrated cell culture helps maintain optimal cell viability and function for experiments. Time-tag separation is clear in bulk and single-cell human-mouse mixes with little cross contamination; doublets remain low under standard loading; and transcript measurements are concordant with 10x Genomics Chromium and bulk references. ChronoSeq also shows high similarity to qPCR measurements of K562 cells stimulated with TNF-α, providing validation with an orthogonal approach. Collectively, these data show that ChronoSeq can introduce reliable time labels at unprecedented time resolutions while maintaining accuracy, cell viability, high throughput and dramatically cutting down on labor requirements for time labelled scRNA-seq.

Applied to TNF-α-stimulated K562 cells, minute-scale sampling resolves an early bifurcation into an inflammatory trajectory with robust NF-κB target induction and a weaker, erythroid-like trajectory. By fitting NB-GAMs within each trajectory, we were able to identify genes with significant temporal dynamics in a principled way. The erythroid branch exhibited distinct kinetics – e.g., transient pulses in CD69 and BIRC3, whereas in the inflammatory branch these genes plateau or continue to rise. For regulatory inference, ChronoPack outperforms traditional methods against both TRRUST and K562 ChIP-seq-based reference networks. This advantage is most pronounced for TFs that are regulated post-translationally without obvious changes in mRNA expression, such as RELA.

In a mixture experiment of K562 and THP1 cells stimulated by LPS, ChronoSeq measures expression profiles that enable the inference of cell-cell signaling. We observed a ~45-minute delay in the K562 NF-κB response compared to THP1, originating from a difference in TLR4 expression by these two cell types. Combining time-resolved ligand-receptor activity scores with a simple ARX/Granger screen nominates mediators that both rise early in THP1 and predict K562 dynamics. Here, we see that TNF interactions with both TNFRSF1A and TNFRSF1B rank highly, recovering established TNF paracrine biology. Importantly, at longer sampling intervals, the relationship between ligand expression and NF-κB response would have been far less evident, limiting the inference of cell signaling from observable lags. This workflow shows how ChronoSeq can prioritize mechanistic hypotheses of cell-cell communication from temporal single-cell transcriptomic measurements alone.

In the context of recent efforts to predict cellular responses to various interventions (drugs, cytokines, and genetic perturbations; see Arc Institute’s Virtual Cell initiative²
), ChronoSeq
provides a complementary, high-resolution view of the immediate transcriptional dynamics following a stimulus. In turn, this allows us to better distinguish direct regulation from indirect effects – an ambiguity that persists when GRNs are inferred from single-snapshot assays such as Perturb-seq.

While ChronoSeq represents a significant advance, its true power will be realized in its application to more complex and physiologically relevant systems. The current throughput, while sufficient for cell lines and major immune populations, may present challenges for profiling very rare cell types in heterogeneous tissues. Furthermore, the transcriptome is only one layer of regulation; a complete "Virtual Cell" model will require future integration with technologies capturing protein activity, chromatin state, and metabolic fluxes at comparable resolution. The logical next step is the fusion of ChronoSeq with precise perturbations to dynamically map the minute-scale consequences of genetic or chemical interventions and build fully predictive models of cellular behavior.

Data Availability
ChronoSeq data are available in the ArrayExpress database (http://www.ebi.ac.uk/arrayexpress) under accession numbers E-MTAB-15894, E-MTAB-15928, E-MTAB-15927, E-MTAB-15946, E-MTAB-15947, E-MTAB-15956, E-MTAB-15955, E-MTAB-15964, E-MTAB-15965 and E-MTAB-15966. Parameters used for each ChronoSeq experiment and the associated accession numbers are listed in Table 1.

Table 1: Experimental parameters used for various ChronoSeq datasets and their accession numbers

Experimental condition | Cell concentration | Time-Tags | Stimulus | Sampling interval | Stimulation time | EMBL-EBI ArrayExpress accession number
K562 | 430 cells/μl | 12 | 10ng/ml TNF-α | 10 minutes | 5 minutes after first sample | E-MTAB-15894
50:50 K562 + differentiated THP1 cells | 430 cells/μl | 12 | 1μg/ml LPS | 15 minutes | 5 minutes after first sample | E-MTAB-15928
K562 | 500 cells/μl | 12 | 10ng/ml TNF-α + 5μg/ml Puromycin | 10 minutes | Both added together 5 minutes after first sample | E-MTAB-15947
K562 Negative Control (Reverse Time-Tag injection order 12 to 1) (QC) | 860 cells/μl | 12 | No Stimulus. Time-Tag Bias estimation | 10 minutes | N/A | E-MTAB-15946
50:50 K562+EL4 (QC) | 215 cells/ μl | 3 | 10ng/ml TNF-α | 10 minutes | 5 minutes after first sample | E-MTAB-15955
50:50 K562+EL4 (QC) | 430 cells/ μl | 3 | 10ng/ml TNF-α | 10 minutes | 5 minutes after first sample | E-MTAB-15956
50:50 U937+K562 | 430 cells/ μl | 12 | 0.5μg/ml LPS | 10 minutes | 5 minutes after first sample | E-MTAB-15927
K562+EL4 (Time Tag 10), K562(Time Tag 11), EL4 (Time Tag 12) (QC) | 215 cells/ μl | 3 | No Stimulus. Only Checking Time-Tags | 7 minutes | N/A | E-MTAB-15964
Bulk K562 and EL4 cells mixed with 12 Time-Tags for verification (QC) | 600 cells/ μl | 12 | No Stimulus. Only Checking Time-Tags | N/A | N/A | E-MTAB-15965
Bulk K562 cells negative control (QC) | 600 cells/ μl | 12 | No Stimulus | 10 minutes | N/A | E-MTAB-15966

Online Methods

Experimental procedures:
Detailed experimental procedures and protocols can be found on the ChronoSeq project website http://wanglab.ucsd.edu/ChronoSeq/ . The notebooks associated with the various protocols also feature embedded YouTube videos. See Supplementary Table S2 for items purchased for assembling the ChronoSeq device. For the latest and most accurate links and information always refer to the protocols and instructions on the project website.

Device design overview

Our device design (Figure S8) addresses several challenges not present in the original Drop-seq⁷ system. See Figure S9 for a comparison and detailed discussion of the ChronoSeq and Drop-seq devices. The system distinguishes itself from conventional Drop-seq devices through several key innovations: automated bead handling with vortex suspension, integrated cell culture system with 37°C water bath and 5% CO₂ environment, robotic droplet collection and bead recovery system, and compressed air pressure control with flow sensing for rapid flow rate changes.

Microfluidic chip design and fabrication

See Figure S10 for a comparison of the ChronoSeq and Drop-seq chip designs and the reasons for the various design changes. For fabrication standard photolithography and PDMS molding techniques⁴⁸ are used for chip fabrication. Chips are plasma bonded to glass slides and chemically treated to create hydrophobic channels. We implemented a rigorous quality control protocol: compressed air testing to check for delamination and eliminate leaking chips, simulating the high pressures used during the flushing phase; visual inspection to ensure the absence of particles before connecting to the device. These design and quality control measures enable the chips to withstand higher pressures and cyclical pressurization during the flushing phase. The optimized chip design is crucial for reliable, high-throughput, time-resolved single-cell sequencing. The improvements in channel geometry and manufacturing process contribute to reduced clogging, increased cell capture efficiency, and overall system robustness. These features are essential for maintaining consistent performance across multiple time points and ensuring high-quality data collection throughout extended experimental runs.

Creation of Time-Tagged ChronoSeq beads from Drop-seq beads

ChronoSeq beads were prepared by modifying Drop-seq beads (Supplementary Figure S3). The modification principle involves binding oligonucleotides (SEQ1 through SEQ12 Supplementary Table S3) to the existing polyT region of Drop-seq beads, followed by extension with E. coli DNA Polymerase I to create the reverse complement of the oligo, and subsequent alkaline denaturation to generate single-stranded DNA. Exact protocol used can be found in Supplementary Protocol 1.

Library preparation
ChronoSeq uses the same oligos used for Drop-seq library preparation (Supplementary Table S3). ChronoSeq library preparation protocol (Supplementary Protocol 2) has an expected yield between 1.5-6ng/ μL after the first PCR reaction as measured by Qubit. While Tagmented sequencing-ready libraries have an expected concentrations of 20-50 ng/μL. Libraries were sequenced on one lane of Illumina NovaSeq X Plus 10B with 10% PhiX Spike-In and Custom Read 1 Primer mixed with Standard Illumina Primers. Either PE100 or PE150 configurations were used for the sequencing run. The ChronoSeq protocol is very similar to the Drop-Seq V3.1 protocol with the following notable changes. First, the Exonuclease 1 treatment step was omitted since it did not contribute to Library yield, quality or capture rates. Next, 14 PCR cycles were typically done instead of 12 PCR Cycles recommended by Drop-Seq for the first round of PCR. Finally, beads were split into different reactions based on number of Timepoints instead of number of estimated STAMPs for both PCR and Reverse Transcription.
Cell culture

All cell lines were cultured in DMEM supplemented with 10% fetal bovine serum (FBS) and 1% penicillin-streptomycin (Pen-Strep) at 37°C in 5% CO₂. THP-1 cells were additionally differentiated into macrophages with 100 nM phorbol 12-myristate 13-acetate (PMA) for 48 hours, then rested for 72 hours. THP-1 macrophages where then converted to a cell suspension non-enzymatically with EDTA to preserve cell surface proteins. Supplementary Protocol 3 provides exact details of cell culture conditions for each cell line.

qPCR validation

K562 cells were sampled with the ChronoSeq device at 10-minute intervals over 2 hours, yielding 12 timepoints. Following baseline sampling, TNF-α (10 ng/μL) was introduced at the 5-minute mark to induce inflammatory signaling. Cell lysates were prepared using a modified Bio-rad SingleShot Cell Lysis Kit protocol (Supplementary Protocol 4) in which the cell suspension was directly mixed with the Lysis reagents instead of washing and changing the media to DPBS.

qPCR validation of K562 co-stimulation by THP1 cells and detection of RNAase activity

To investigate paracrine signaling effects between immune cell populations, THP-1 cells were differentiated and stimulated with 1 μg/ml LPS, with cell supernatants collected at 0, 1, 2, and 3 hours post-stimulation. These time-course supernatants were then applied to K562 target cells. Controls included unstimulated K562 cells and K562 cells stimulated with TNF-α. K562 cells were sampled at 0 and 1 hour following supernatant addition using a modified Bio-rad SingleShot Cell Lysis Kit protocol (Supplementary Protocol 5). Next, we performed qPCR for the relatively lowly expressed housekeeping gene HPRT1 in some of the same samples of K562 cells stimulated with THP1 supernatants and controls (Fig. S7). HPRT1 was not detected in all samples stimulated with THP1 supernatants, with no Cq values generated (See Table S1). Based on the same data we also observed no RNAase activity for K562 cells stimulated with TNF-α. This confirmed high RNAase activity is a problem unique to THP1 cell suspensions. Thus, we added 3U/ul of Watchmaker Genomics RNAase inhibitor at 800U/ul was added to each Time-Tag for our THP1-K562 mixture experiment.

Computational procedures:

ChronoSeq-Tools pipeline

The ChronoSeq-Tools pipeline extends the Drop-seq pipeline methodologies to enable temporal tracking of single-cell transcriptomes through integrated Time-Tags. The pipeline processes paired-end RNA sequencing data through sequential barcode extraction, alignment, and Time-Tag determination phases to generate a final Digital Gene Expression matrix (DGE) with Time-Tags for each Cell. Scripts and instructions for running the ChronoSeq-Tools pipeline can be found on GitHub https://github.com/kanishkasthana/ChronoSeq-Tools . Moreover, code for generating QC plots in this paper can be found at https://github.com/kanishkasthana/ChronoSeq-QC

Pipeline architecture

The workflow initiates by converting FASTQ files to unaligned BAM format using Picard's FastqToSam. Three sequential tagging steps employ Drop-seq's TagBamWithReadSequenceExtended to isolate:

1. Cell barcodes (XC tag: bases 1-12)
2. Unique molecular identifiers (XM tag: bases 13-26)

3. Time-Tags (YT tag: bases 27-86) with relaxed quality thresholds (≤150 low-quality bases permitted).

Quality control steps include filtering reads with low-quality tags and trimming adapter sequences (AAGCAGTGGTATCAACGCAGAGTGAATGGG) and polyA tails using Drop-seq tools. Processed reads undergo STAR alignment against species-specific references, followed by queryname sorting and MergeBamAlignment to preserve metadata. Gene annotation occurs via TagReadWithGeneFunction using RefFlat files, generating digital expression matrices(DGEs). Computational efficiency is enhanced through optional scratch directory usage and distributed locking mechanisms to manage I/O operations on SLURM cluster systems.

Alignment references
For species-mixing experiments reads were aligned to the same hg19-mm10 mixed cell reference used in Dropseq. For all other experiments hg38 was used for alignment.

Time-Tag determination

Time tags derive from twelve synthesized oligonucleotides containing a combination of degenerate bases (R,Y,M,K,S,W,H,B,V,D,N) and constant bases flanked by polyA sequences. The GetTimeTags algorithm:

1. Extracts YT tag sequences from aligned BAM files
2. Performs reverse complement conversion
3. Matches sequences against regex patterns for each Time-Tag.
4. Requires ≥20 detections per cell barcode for reliable assignment.
5. Assigns final Time-Tags through majority vote (≥70% prevalence) for each Cell barcode. Cell barcodes failing to meet this threshold are flagged as having "Time Tag Collision Detected" indicating potential cross-contamination or sequencing errors

Comparison with Drop-seq pipeline

While sharing core components (Picard, Drop-seq tools, STAR alignment), ChronoSeq introduces three key modifications:

Feature | Drop-Seq | ChronoSeq
Barcode Structure | 12bp cell + 8bp UMI | 12bp cell + 14bp UMI + 60bp time tag
Tag Quality Threshold | Strict (1-2 errors) | Permissive for time tags (150 errors)
Output | Gene expression | Expression + temporal stratification

Optional error correction

ChronoSeq supports optional error correction for both substitution and synthesis errors in cell barcodes, closely mirroring Drop-seq’s established methodology. Our substitution error correction has been optimized to run on multiple cores to speed up execution. Like Drop-seq the correction step identifies cell barcodes differing by a single base (Hamming distance of 1) and collapses those with a dominant sequence representing at least 93% of reads, mitigating sequencing errors. The synthesis error correction step identifies and collapses barcodes with systematic errors at the barcode termini, typically arising from bead synthesis imperfections. This is accomplished by constructing a Prefix-Trie data structure and merging barcodes that differ only at the last few positions, replacing the error-prone bases with 'N' and updating associated UMIs accordingly. Using a Prefix-Trie approach allows us to speed up execution from Quadratic to Linear time for our approach compared to Drop-Seq. These corrections are performed prior to digital gene expression quantification and time tag assignment, ensuring high-fidelity cell barcode recovery

ChronoPack package:

Standard preprocessing. Time-Tagged ChronoSeq DGE data generated using the ChronoSeq-Tools pipeline was processed using the standard Scanpy⁴⁹ workflow. Quality filters were applied to remove cells with too few counts (<200 genes, <500 UMIs), as well as potential doublets (>15000 UMIs) or damaged cells with mitochondrial expression percentage >7.5. Cells predicted to be doublets via Scrublet⁵⁰ were also removed. The filtered gene-count matrix was library normalized and log transformed (sc.pp.normalize total, sc.pp.log1p). Each cell was assigned S and G2M phase scores using sc.tl.score genes cell cycle based on cell cycle marker genes from Kowalczyk et al, 2015⁵¹. The dataset was subset to the top 3000 highly varying genes using sc.pp.highly variable genes.

Expression correction. Technical factors (total UMIs, percentage of mitochondrial expression) and cell cycle effects (S and G2M scores) were regressed out prior to applying ComBat⁵² to correct for different reverse transcription batches. The corrected expression matrix was scaled using sc.pp.scale, followed by sc.tl.pca to calculate principal components (PCs). Reduced embeddings for each cell were selected as the top n PCs, where the optimal value of n was selected by plotting PC variance ratios and identifying the elbow (i.e., the point of maximum curvature).

Metacell construction. Similarly to Sheu et al, 2024⁵³, metacells were constructed via k-means clustering within each time point using these embeddings. A default value of k = (20 × number of cell types) was used. Raw counts for cells assigned to the same metacell were aggregated, followed by library normalization and log transformation. Importantly, no obvious batch effects were observed in the resulting metacells as they were aggregated from cells that were similar in the corrected expression space.

Deriving a transition kernel from optimal transport couplings. WaddingtonOT³⁰ was used to infer transport couplings between metacells across successive time points (i.e. from t to t+1). Default parameters for the entropy, row sum, and column sum regularization terms were used (ϵ=0.05, λ1=1, λ2=50). The resultant couplings were stitched together into a sparse transport matrix T with Tij encoding the descendant mass sent from cell i to cell j. The forward transition kernel is the row-normalized form of this matrix, calculated as P = D⁻¹
T where D = diag(T1), and
Pij is the probability of cell i transitioning to cell j. P enables us to (a) map cell fates and (b) impute gene expression changes from forward and backward expectations on P.

Cell-wise trajectory clustering. We hypothesized that the transition kernel could be used to cluster cells by their temporal responses. The expected fate distribution from a random walk of length k can be calculated as Sk = Pk where Sijk represents the probability that cell i walks to cell
j. A weighted average across length k = 1...K random walks can then be constructed as S = sum

λk
Sk. Here, λ is a hyperparameter that can be tuned to discount longer random walks; smaller values of λ favor higher Sij for cells that are temporally proximal. Finally, this matrix was symmetrized as W = (S + ST
)/2 such that higher edge weights corresponded to metacell pairs i, j if either one was reachable from the other across multiple steps forward in time. Finally, the Leiden algorithm was applied to W to assign clusters corresponding to different trajectories. These clusters on W correspond to communities of metacells that share similar futures and pasts according to P.

Cell fate mapping. Terminal fates were identified as the last metacells belonging to either trajectory cluster. Fate probabilities are traditionally calculated by converting P to an absorbing Markov chain and solving the linear system (I − Q)X = R where Q ≡ transitions between transient states, R ≡ transitions from transient to absorbing states (i.e., terminal fates), and I is the identity matrix⁵⁴. However, since WaddingtonOT edges are strictly directed forward in time, P forms a directed acyclic graph for which fate probabilities can be estimated through a dynamic programming approach. Let pk(i) denote the probability that a random walk starting at cell i is ultimately absorbed in terminal fate Ak. By setting the boundary conditions pk(i) = 1 for i ∈ Ak and pk(i) = 0 for i /∈ Ak, a reverse-time sweep can be performed recursively via pk(i) = sumj Pij · pk(j) to recover fate probabilities pk for all cells. Fate uncertainty was then calculated as the Shannon entropy H(i) = −sumk pk(i) · log(pk(i)). Finally, we identified early genes that were predictive of trajectory branch choice by correlating per-metacell expression in the earliest time bin with a fate-contrast score. Specifically, for each early metacell i, we defined the fate contrast as yi = p1(i) − p0(i). After removing genes detected in <10% of early cells, Spearman rank correlations were computed. P-values were adjusted for multiple testing via Benjamini-Hochberg. Significant positively and negatively correlated genes were labeled as being associated with fates A1 and A0, respectively.

Identifying genes with significant temporal trends. For each gene, the tradeSeq³¹ package was used to fit a negative-binomial generalized additive model (NB-GAM), where mean expression is modeled as a cubic smoothing spline function over real time. Metacell counts are modeled with a negative binomial distribution Ygi ∼ NB(µgi, ϕg), where log(µgi) = suml sglZli +log(Ni). Here, Ni are library size offsets, Zli denotes metacell membership in each lineage, and sgl = sumk bk(t)βglk is a smoothing spline constructed from cubic basis functions bk(t). A basis size of K=8 was used. After fitting, tradeSeq’s associationTest function was used to compute a Wald test statistic assessing the null hypothesis that all coefficients are equal, i.e., H0: βglk = βglk′. The associated p-values were adjusted for multiple testing via Benjamini-Hochberg, and genes with q<0.05 were labeled as significantly trending over time. These genes were clustered by the similarity of their trajectory-wide expression patterns using tradeSeq’s
clusterExpressionPatterns method.

Gene regulatory network inference. Traditionally, GRN inference methods predict a ranking of TF-gene edges which can then be benchmarked against a ground-truth network. In our experiments, stimuli such as TNF-α or LPS induce changes in gene expression primarily through the post-translational modification of TF activity. In this context, co-expression modeling cannot be used to infer regulatory edges, as is done in GRNBoost2 and similar methods. Instead, we developed an inference strategy that independently ranks (i) TFs as being downstream of a stimulus (i.e., which TFs are most likely to be perturbed) and (ii) target genes as being impacted by that same stimulus, prior to fusing these rankings together via the Borda method to infer TF-gene regulatory edges.

To score TFs as being perturbed by a stimulus, we utilized PPI and signaling pathway annotations from OmniPath³³. We first construct a directed, signed intracellular signaling network centered on the stimulus of interest (e.g. TNF) using OmniPath's PostTranslational interactions. Edge signs in this directed network were encoded as +1 (stimulation), -1 (inhibition), or 0 (unknown) based on OmniPath's is_stimulation/is_inhibition flags. An expression filter was applied to restrict the graph to proteins that were likely to be active, where nodes were excluded if their corresponding RNA transcripts were detected in fewer than 1% of cells. Next, we enumerated all directed signaling paths from the ligand to each TF and summarized these paths into TF-level scores. We performed a depth-first traversal starting at the ligand (i.e., stimulus) of interest: the first hop used curated ligand-receptor pairs from CellChatDB, and all subsequent hops followed the directed, signed OmniPath graph up to a fixed radius of 5 steps. TF nodes were treated as sinks, so paths terminated once they reached a TF. For each distinct stimulus → TF path, we tracked the cumulative sign si (i.e., the product of edge signs) from the stimulus to the TF. Each path was assigned a weight that decayed exponentially with path length, allowing for shorter paths to contribute more, and was also multiplied by a branching penalty B that downweighted routes passing through higher-degree nodes (W! = B!δ"!#$ where δ = 0.7). The final score for the TF was taken as ∑ s!W!, summing the weights and cumulative signs of all paths i terminating at that TF. Target genes were ranked by the Wald statistic corresponding to tradeSeq's associationTest, where larger values corresponded to a more significant temporal trend. The TF- and target gene-specific rankings were then combined via a modified version of the Borda method to produce an overall ranked TF-gene edge list.

GRN inference was benchmarked against other co-expression-based methods, including GRNBOOST2, GENIE3, SINCERITIES, and PPCOR. Early precision ratio (EPr) and areaunder-precision-recall-curve ratio (AUPRCr) were calculated to assess the performance of the predicted networks. We focused on evaluating these metrics per TF subnetwork, as well as the subnetwork spanned by all NF-kB-relevant TFs, provided that these TFs were also available in the ground-truth network. We considered three ground-truth networks: (a) the TRRUST⁴⁰ database, which contains literature-curated human TF-gene interactions, and (b-c) two K562-specific networks derived from ChIP-seq experiments. For the latter category, ChIP-seq peaks were either (b) retrieved from the ENCODE³⁸ project for the human K562 cell line, corresponding to 1670 experiments and 757 unique accessions or (b) taken directly from CausalBench³⁹, which constructed its own ground-truth network in which edges were further filtered according to perturbation effect sizes.

Cell-cell communication. Ligand-receptor (L-R) pairs annotated as ’Secreted Signaling’ were queried from CellChatDB⁴⁴. In our experiment, the THP1 NF-kB response preceded that of the K562 cells, so we focused specifically on pairs where the ligand and receptor were adequately expressed (>5% with nonzero counts) in the THP1 and K562, respectively. We also required the corresponding ligands to vary significantly over time per our earlier NB-GAM statistics (q<0.05). This filtering procedure resulted in 10 candidate ligand-receptor pairs out of an initial set of 1199 interactions. Next, an L-R activity series ALR(t) = sqrt(µTHP1

L(t)µK562
R(t)) was constructed as the geometric mean of the fitted means on the log1p scale. The K562 NF-kB response series y(t) was calculated as the per-time-bin average of a curated NF-kB module. To assess the relationship between the L-R activity and NF-kB response in K562 cells, we conducted a singlelag Granger⁴⁵ screening. For each lag L ∈ [2, 5] and candidate L-R pair, we fit an ARX (autoregressive with exogeneous input) model yt = c + (α·yt−1) + (β·xt−L) + ϵt. We tested H0: b=0 via a partial F-test, comparing the restricted model (i.e., no xt−L) against the unrestricted model. To limit the space of feasible lags, we enforced a sign constraint by discarding lags with a negative cross-correlation cor(yt, xt−L), corresponding to the assumption that the presence of a ligand, rather than its absence, induces a signaling response in the K562 cells. The Holmadjusted within-pair p-values were subjected to Benjamini-Hochberg (BH) correction across pairs. While pairs with q<0.05 were considered statistically significant for visualization purposes, we primarily focused on the utility of these test statistics for prioritizing L-R pairs as candidates for cell-cell communication. Alternatively, we performed a lead-lag correlation test to assess the association between ALR and y, which produced a similar ranking of the L-R pairs.

Supplementary Figures and Tables

Supplementary Figure S1. a) Shows the current paradigm for a temporal drug response study. If twelve timepoints are taken over two hours, each timepoint would have to be processed independently. Optimistically if five hours of hands-on labor is needed for each timepoint, this would require a minimum of 60 hours of total hands-on labor for all timepoints. Due to the lack of automation and manual nature of the technology there is a high possibility of inconsistent sampling or labelling times for each time point. For example, in each sample the metabolites used for labelling need to be washed out. Washing out is not instantaneous and the cells have time to incorporate more metabolites during processing delays; thereby increasing the chance of introducing an error of several minutes or longer for each sample. An error of several minutes introduces the high possibility of measuring spurious perturbations, especially if the sampling rate is also several minutes. Therefore, the high labor requirement, lack of automation, separate labeling of each sample, no immediate cell lysis to preserve transcriptome and resulting minute-scale sampling/labelling errors, make it practically impossible to use metabolic labelling for profiling real-time perturbations over several hours. b) If this same temporal drug response study is done using ChronoSeq this would require only five hours of hands-on labor. Moreover, by automating sample collection across time points and consolidating them into a single library via time-barcoded beads, ChronoSeq achieves minute-level sampling of expression dynamics over multiple hours. Automation and the immediate cell lysis help eliminate human errors in sampling and labelling, while integrated cell culture helps maintain optimal cell viability and function for experiments.

First Timepoint Injection | Second Timepoint Injection

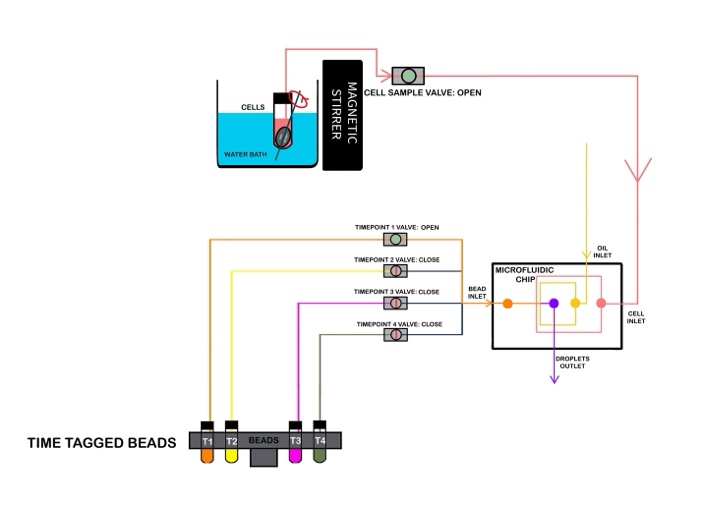
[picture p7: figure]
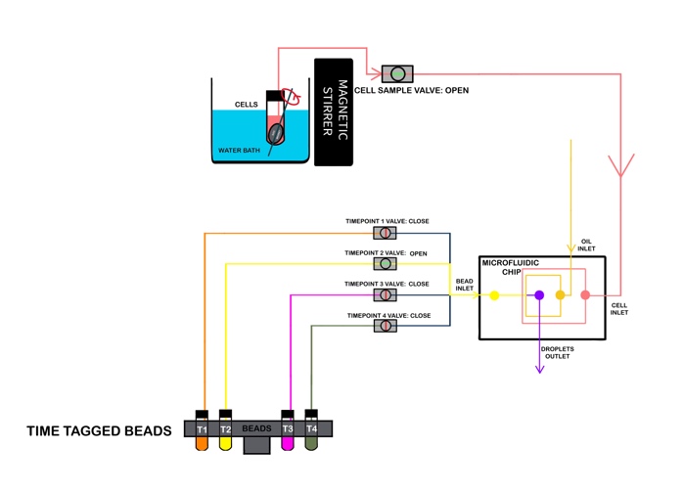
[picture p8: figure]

Third Timepoint Injection | Fourth Timepoint Injection

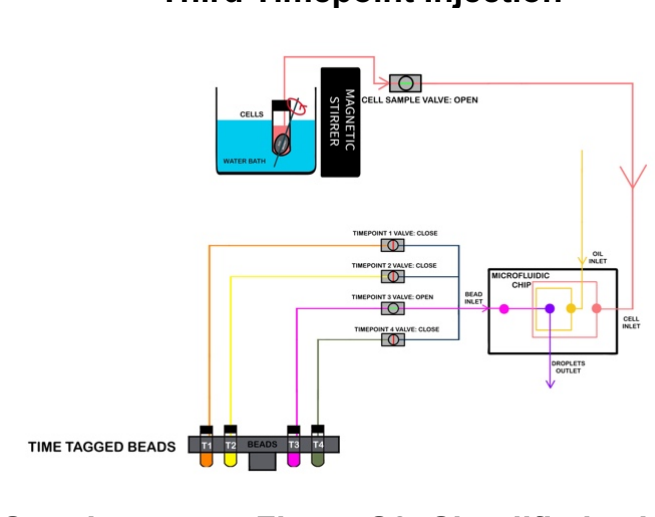
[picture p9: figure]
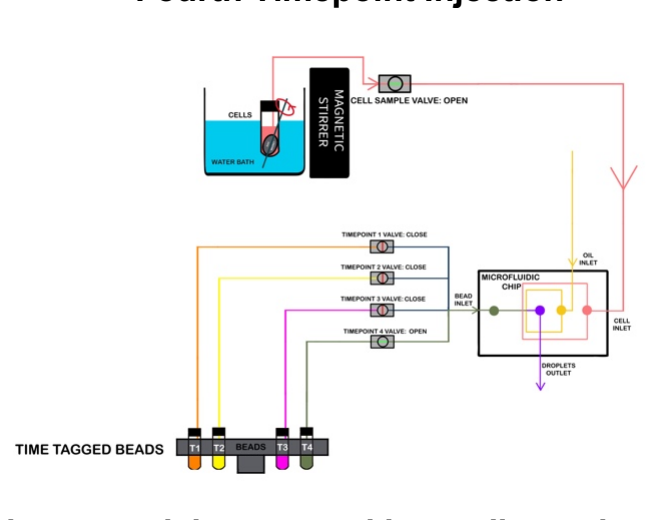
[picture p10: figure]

Supplementary Figure S2: Simplified schematics to explain temporal barcoding using ChronoSeq device. The device sequentially co-injects Time-Tagged beads and cells into a droplet-generating microfluidic chip at regular time intervals. These beads are stored in separate reservoirs (e.g., 4 reservoirs for 4 time points for illustration purpose), with each reservoir containing beads with a unique Time-Tag. For each timepoint, the Cell Sample Valve remains open while the corresponding Timepoint Valve (orange for T1, yellow for T2, Hot Pink for T3, and Olive Green for T4) is opened. This allows for the co-injection of time-specific beads with cells, resulting in libraries barcoded with distinct Time-Tags. This process enables precise temporal labeling of cells across different timepoints. Our system currently supports 12 unique Time-Tags with minimum 7-minute intervals including a 1-minute sampling duration.

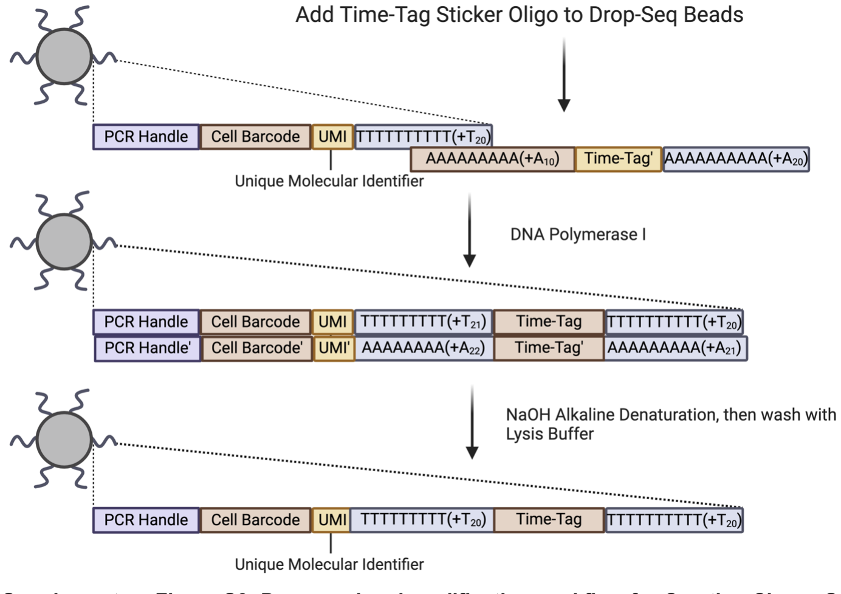
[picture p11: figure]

Supplementary Figure S3: Drop-seq bead modification workflow for Creating ChronoSeq Time-Tagged beads. Sequences are added by using an oligo that binds to the existing PolyT region on Drop-seq beads. The 3’ end of the Drop-seq beads are then extended to the reverse compliment of the oligo using E. Coli DNA Polymerase I. Alkaline denaturation is used to make the double stranded DNA single-stranded. These beads are then resuspended in lysis buffer and can be used directly with our device.

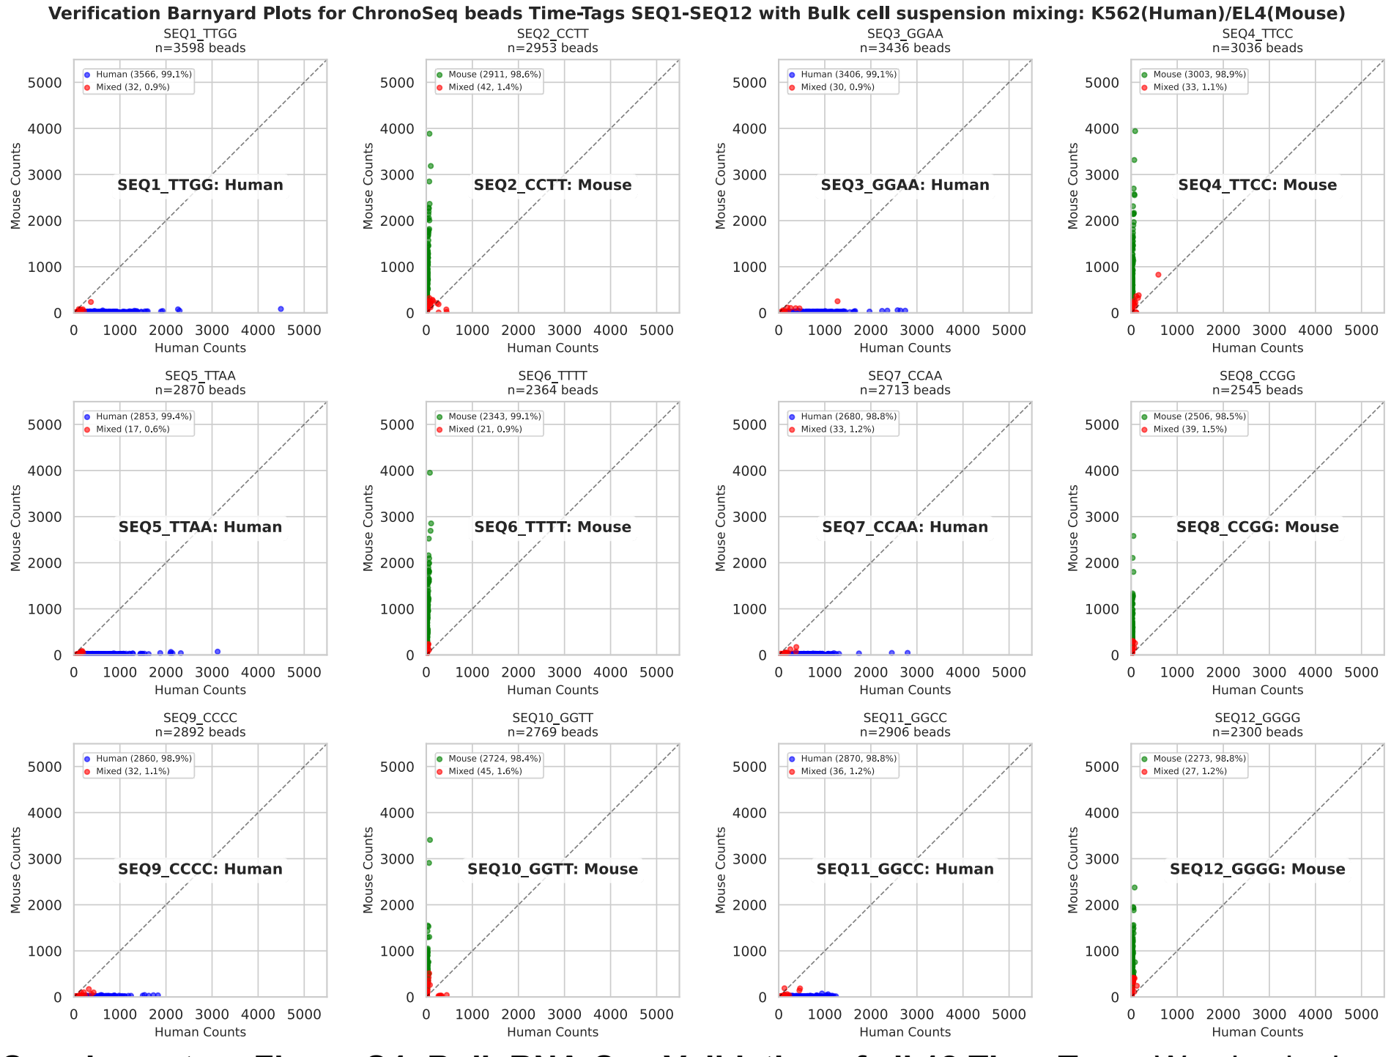
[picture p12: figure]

Supplementary Figure S4: Bulk RNA-Seq Validation of all 12 Time-Tags. We checked our ability to uniquely identify each Time-Tag. We did this by mixing beads from odd numbered Time-Tags with human cells and even numbered Time-Tags with mouse cells manually in bulk. These beads were then washed and combined for reverse transcription, library preparation and sequencing. Time-Tag resolved cleanly into either human or mouse dominant with 1.6% or less mixed beads detected for each Time-Tag.10μl of Time-Tagged beads at 450 beads/μl suspended in lysis buffer were directly mixed with 8μl of mouse or human cells at 600cells/μl. Odd numbered Time-Tags were mixed with human(K562) cells while even numbered Time-Tags were mixed with mouse(EL4) cells. Each dot in the scatterplots represents a anique Cell Barcode and the (X, Y) coordinates represent the number of human and mouse transcripts captured respectively. Each plot is also labelled with the which species of the cells were mixed with the beads for the experiment.

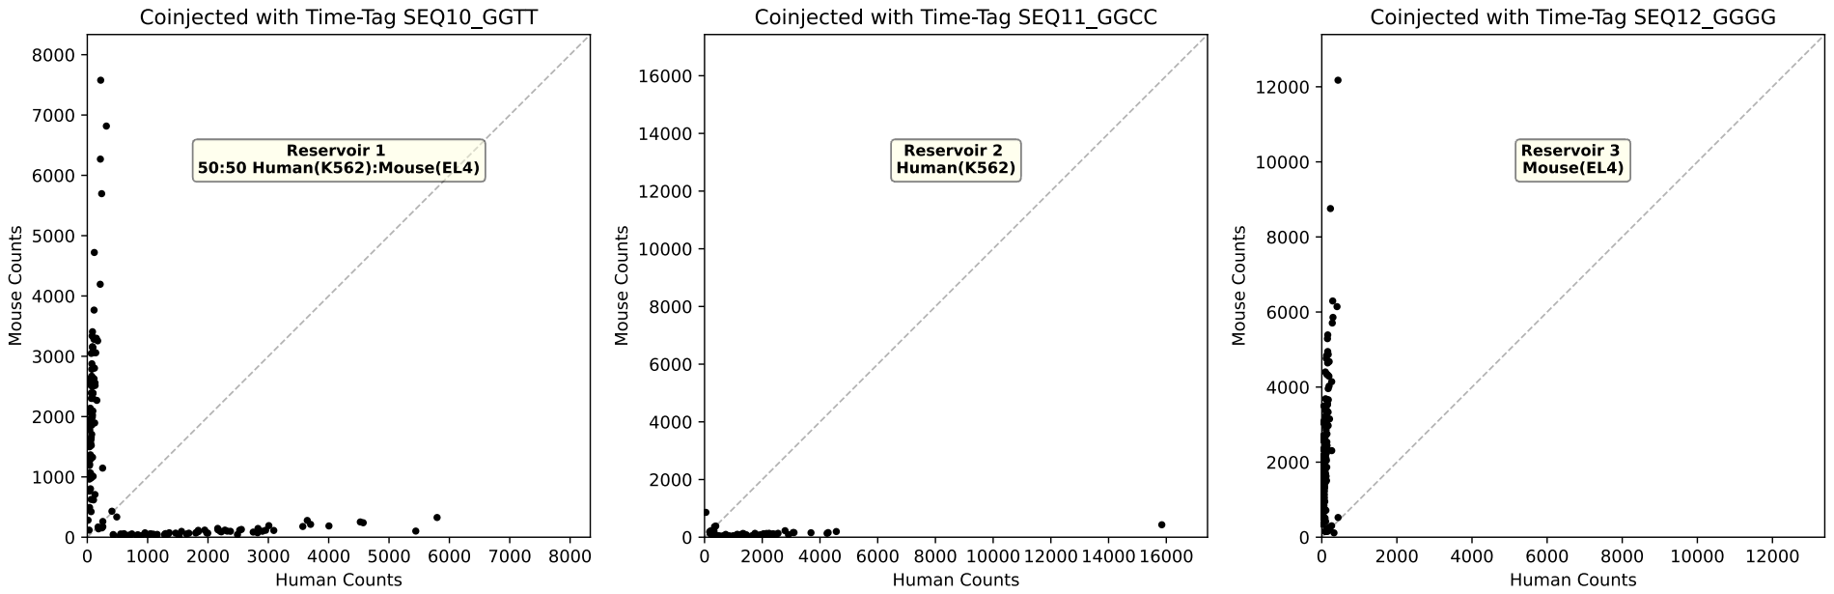
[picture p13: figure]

Supplementary Figure S5: Single-Cell ChronoSeq Experiment to verify unique Time-Tagging: We checked whether the ChronoSeq device could uniquely tag each sample with a Time-Tag without mixing across samples. To do this we setup three separate reservoirs for maintaining cell suspensions inside the ChronoSeq device. Cell could be sampled from either Reservoir 1, 2 or 3 and co-injected with any of the Time-tagged beads labeled 1-12. A 50:50 mixture of human(K562) and mouse(EL4) cells was added to Reservoir 1, a human only (K562) suspension to Reservoir 2 and a mouse only(EL4) suspension to Reservoir 3. Cells were sampled with a 7-minute sampling interval including a 1-minute sampling duration using the ChronoSeq device. The first sample (left) was from a 50:50 Human(K562) and Mouse(EL4) Cell Suspension. The second sample (center) was from a Human only cell suspension. While the third sample (right) was from a Mouse only cell suspension. Each dot in the three plots represents a Unique Cell Barcode and the (X, Y) coordinates represent the number of Human and Mouse transcripts respectively. Cells were injected at a concentration of 215 cells/μl while the bead concentration was 450 beads/μl. The first, second and third cell suspensions were sequentially co-injected with Time-Tags 10 through 12. Species-mixing barnyard plots clearly showed Time-Tag 10 capturing both human and mouse cells, Time-Tag 11 capturing human cells and Time-Tag 12 capturing mouse cells.

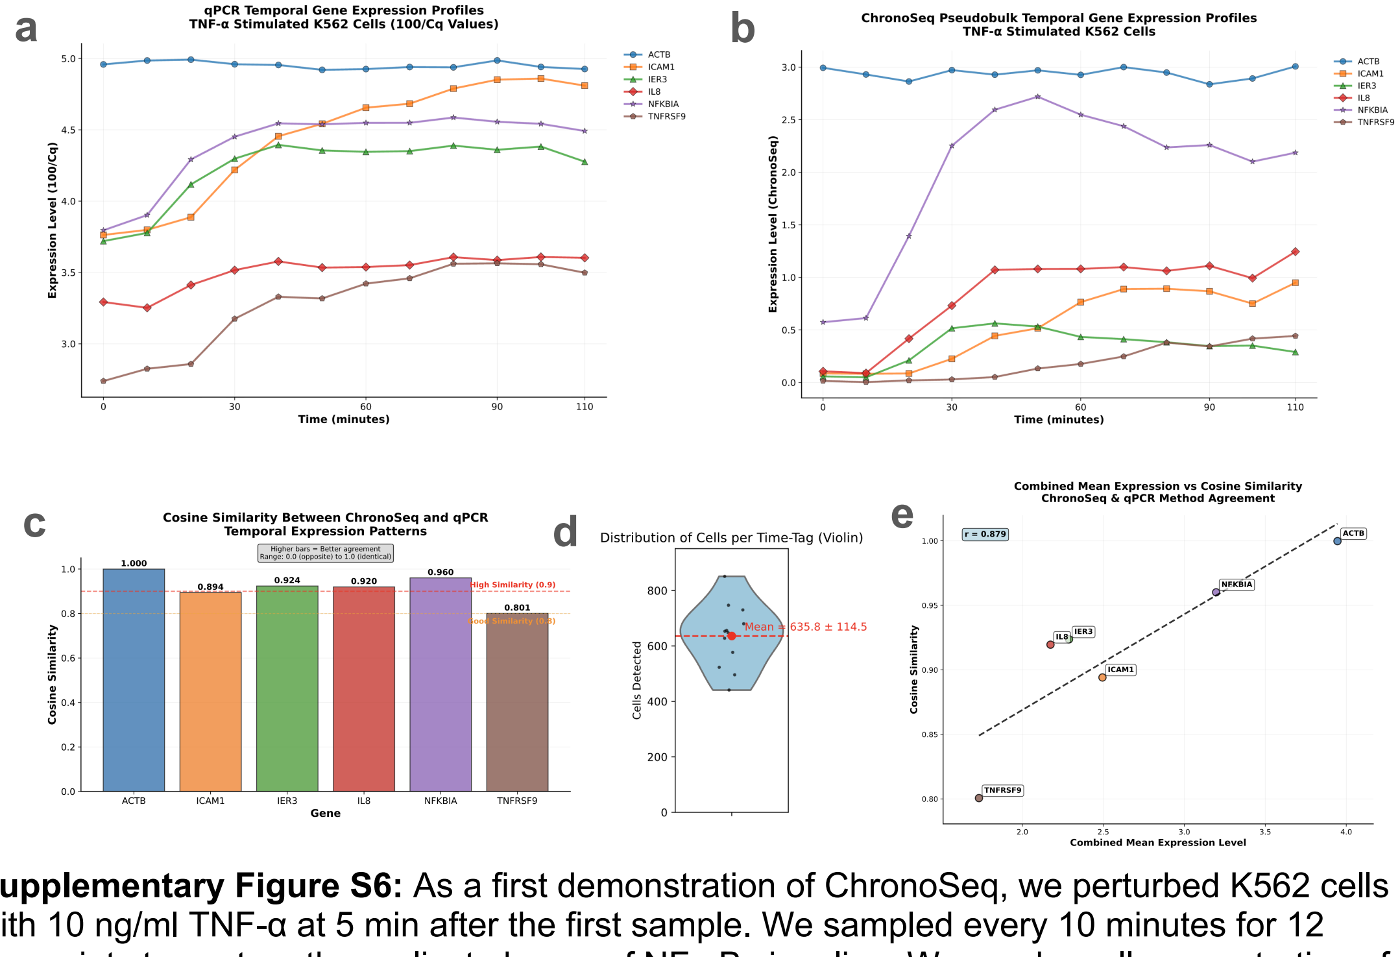
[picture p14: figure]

Supplementary Figure S6: As a first demonstration of ChronoSeq, we perturbed K562 cells with 10 ng/ml TNF-α at 5 min after the first sample. We sampled every 10 minutes for 12 timepoints to capture the earliest phases of NF-κB signaling. We used a cell concentration of 430 cells/μl and a bead concentration of 450beads/μl for all Time-Tags. To validate the temporal response, we performed a qPCR measurement with the same time resolution of 10 minutes for K562 cells stimulated with TNF-α. We show 5 representative genes and one housekeeping gene (ACTB) and compare it to the pseudobulk of the same genes obtained from the single-cell ChronoSeq data. The temporal profiles (a-b) showed good to high concordance (measured by cosine similarity, c) with higher expressed genes showing higher similarity, thus less affected by noise, compared to lower expressed genes (e). We captured an average of 636 cells per Time-Tag. (d) shows a violin plot of the number of cells we captured per Time-Tag for this experiment.

Supplementary Figure S7: We validated the lack of responsiveness for K562 cells with a qPCR experiment where supernatants from THP1 cells stimulated with LPS were added to K562 cells at different times after LPS stimulation. NFBKIA was measured as a marker of the inflammatory response in K562 cells and ACTB was measured as a control. K562 supernatants show strong activation for supernatants taken after 1 hour or longer from THP1 cells: (a) NFKBIA fold changes were calculated using the 2⁽⁻ΔΔCq) method⁵⁵ with ACTB as the housekeeping gene and unstimulated K562 cells as the reference control. Temporal dynamics were visualized by plotting fold change values against THP-1 supernatant collection time (0, 1, 2, 3 hours post-LPS stimulation). Two K562 measurement timepoints were compared: baseline (T=0, immediately after supernatant addition) and 1-hour post-treatment (T=1h). Data points represent mean values from n=2 technical replicates. Plots clearly show K562 response to stimulation with THP-1 supernatants collected at 1 hour with double the fold change. To further show that K562 cells cannot respond to LPS either alone or when mixed with cells unresponsive to LPS; we LPS stimulated a 50:50 mixture of K562 and undifferentiated U937 cells which are known to show limited or no response to LPS⁵⁶. Unlike the pseudobulks of NFKBIA and ACTB in K562 cells stimulated with TNF-α (Fig. S6(b)), the U937:K562 mixture shows no response: (b) Pseudobulks for scRNA-seq generated for ACTB and NFKBIA genes from a 50:50 U937 and K562 cells mixture stimulated with 0.5ug/ml LPS inside the
ChronoSeq device. Samples were taken every 10 minutes for 12 timepoints, with LPS addition 5 minutes after first sample. This lack of response is similar to NFKBIA and ACTB pseudobulks from the K562 negative control experiment: (c) Pseudobulks for scRNA-seq generated for ACTB and NFKBIA genes from the K562 negative control experiment.

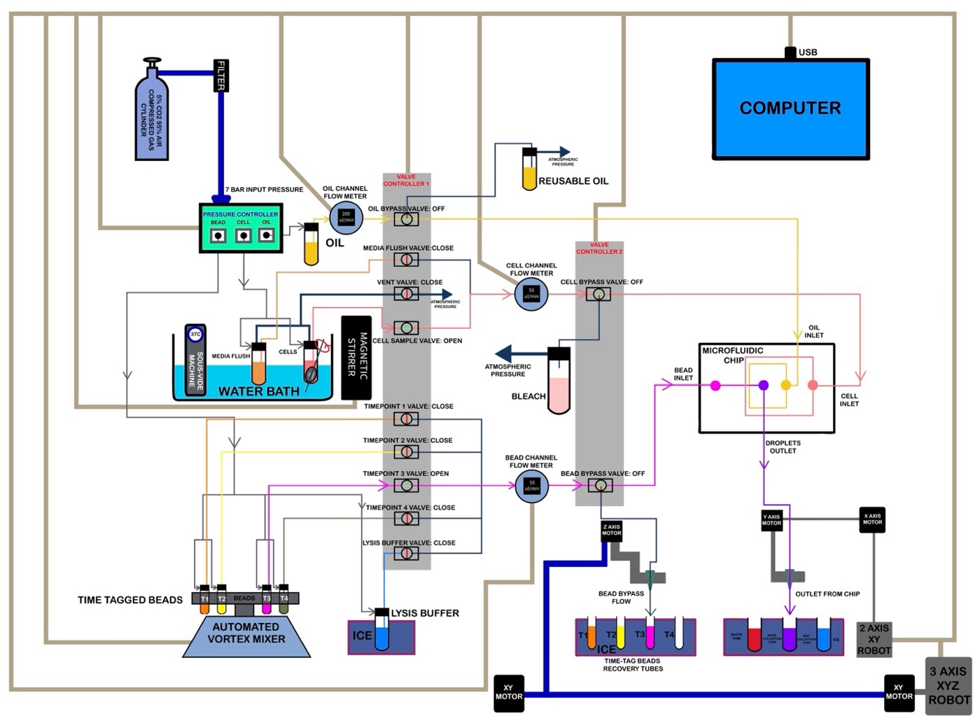
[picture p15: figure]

Supplementary Figure S8: ChronoSeq device full schematic

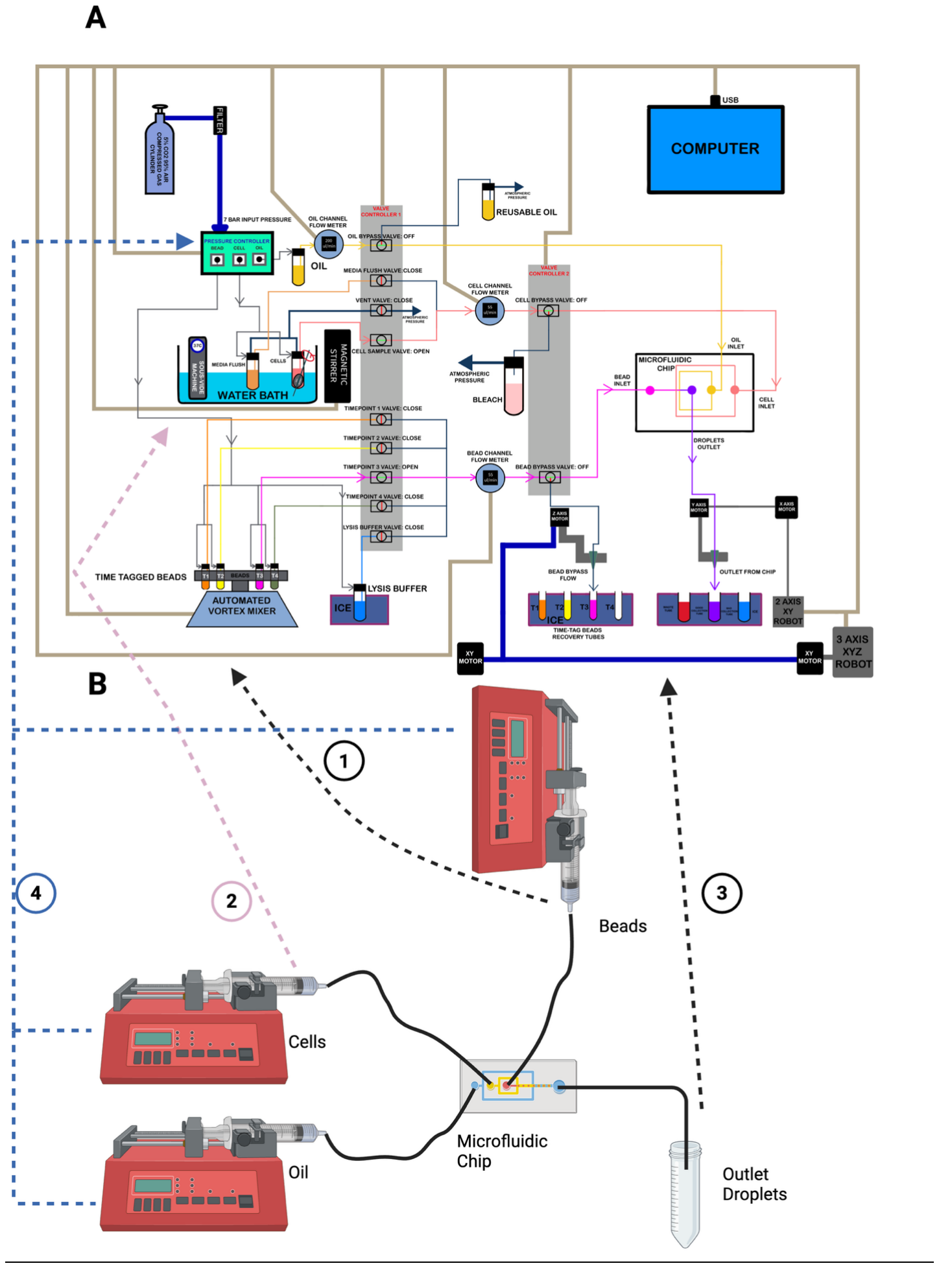
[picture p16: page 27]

Supplementary Figure S9: Comparison of ChronoSeq and Drop-seq devices

Our device design addresses several challenges not present in the original Drop-seq⁷ system. First, extended cell viability. We maintain cell suspension viability for experiments lasting 2 hours or longer, compared to typical 30-minute Drop-seq runs. Second, cross-contamination prevention. We implemented a washing system to remove unused cells or beads between samples. Third, sample isolation. We designed a system to prevent mixing wash fluid with droplets. To address these challenges, our device operates in two main phases during each injection cycle. 1. Flushing phase that clears fluid lines of residual beads or cells from previous injections. 2. Injection phase that precisely introduces cells and Time-Tagged beads into the microfluidic chip. This integrated system enables controlled, sequential introduction of cells and Time-Tagged beads, capturing gene expression dynamics across multiple time points in a single experiment. Our design prioritizes cell viability maintenance, precise fluid control, and efficient bead usage, all critical for generating high-quality, time-resolved single-cell sequencing data.

The ChronoSeq device is controlled via serial connections to a computer, which coordinates the actions of its various components, while the Drop-seq device works by setting flow rates manually on syringe pumps. Some key features distinguish the ChronoSeq device:

1. Bead handling: ChronoSeq incorporates an automated vortex mixer to keep the beads evenly suspended before injection. Drop-seq uses a magnetic stirrer for bead suspension, which leads to high dead volumes and complicates automation for multiple Time-Tags. ChronoSeq allows for the easy addition of more Time-Tags in the future if necessary. Additionally, loading and unloading the beads is simplified; we can directly screw a new 50 mL tube containing beads into the reservoir. The Time-Tagged bead reservoirs are connected to timepoint valves, which facilitate the selection of the appropriate Time-Tagged beads for injection into the microfluidic chip.
2. Cell culture system: In the Drop-seq device, cells are directly loaded into a syringe for injection, typically running for 15 to 30 minutes. However, our goal is to maintain cell viability for at least 2 hours. Leaving cells at room temperature without growth media and in the absence of 5%
CO2 can lead to excessive cell death and unwanted perturbations. To address this, we have integrated a cell culture system directly into the ChronoSeq device, featuring a water bath to maintain cells at 37°C, along with a 5% CO2 gas cylinder that serves as a pressure source and aids in cell culture. Furthermore, we can add additional tubes to culture multiple cell suspensions separately and use valves to select which cell suspension is injected into the microfluidic chip.
3. Droplet collection: In the Drop-seq device, droplets are collected directly in a 50 mL tube kept on ice. However, in our system, it is crucial to prevent the beads and cells from previous injections from mixing with those from new injections. To achieve this, we developed a washing system to clear the fluid lines of residual beads and cells. We also need to ensure that washing liquids and unused cell suspensions do not mix with the collected droplets. To solve this issue, we designed a robotic system that facilitates droplet collection and bead recovery. This robot automatically moves the outlet tubing to the correct tube, preventing the mixing of droplets with washing fluids. Additionally, it can recover unused beads from the fluid lines, minimizing waste and reducing experimental costs. Like the Drop-seq device, the droplets in our system are also kept on ice using ice boxes.
4. Flow control: In the Drop-seq device, precise speed control is essential for droplet formation. Speeds that are too high can inhibit droplet formation, while low speeds can negatively impact throughput. To achieve this precise control, Drop-seq employs syringe pumps, which allow direct manipulation of the syringe's squeezing rate. In our case, we require high flow rates for flushing and low flow rates for droplet formation. Low flow rates like Drop-seq flow rates, are insufficient for quickly washing unused beads and cells from the device. Therefore, we implemented a compressed air pressure controller and flow sensors for each of the bead, cell, and oil channels. The compressed air controller enables rapid changes in flow rate, while the flow sensors provide the precise control needed for high-quality droplet formation during low flow rate operation.

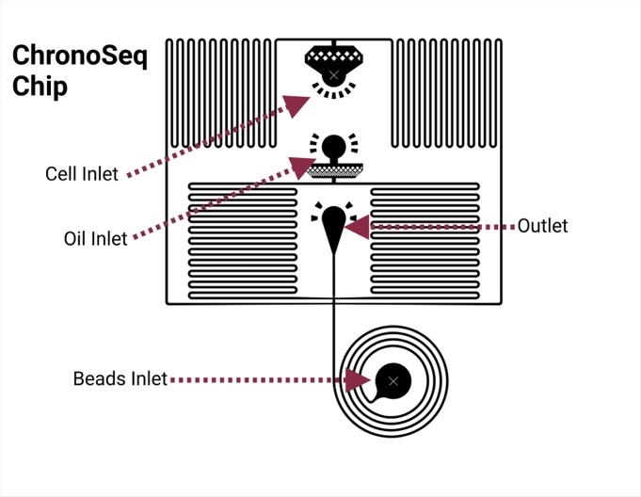
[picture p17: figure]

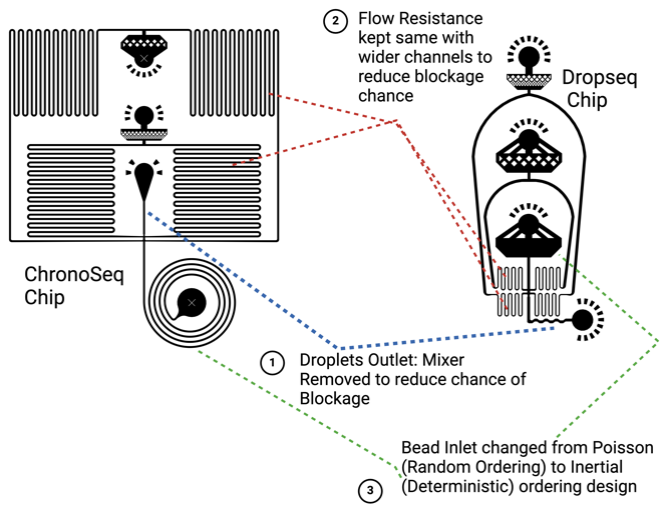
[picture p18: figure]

Supplementary Figure S10. ChronoSeq microfluidic chip. The primary function of the microfluidic chip is to co-encapsulate cells with Time-Tagged beads using a flow-focusing junction⁵⁷ at the center of the chip. While we initially considered using the Drop-seq device for this purpose, several limitations made it unsuitable for our application: 1. Ordering mechanism. Drop-seq relies on random (Poisson) ordering for co-encapsulation of cells and beads. This random ordering makes it difficult to increase the number of cells collected per timepoint without also increasing droplets containing multiple cells or beads. The ChronoSeq microfluidic chip uses an optimized version of an existing inertial ordering design⁵⁸ to increase cell capture through deterministic ordering of beads into droplets. This deterministic ordering allows for capturing more cells by increasing the number of droplets containing exactly one bead and one cell. 2. Channel design. Both the Drop-seq chip and existing inertial ordering⁵⁸ designs use narrow flow resistance channels, which are prone to blockage during the flushing phase. To reduce blockage risk, we widened the channels in our chip design. To maintain the same flow resistance with wider channels, we increased the length of the channels to compensate.

Left, ChronoSeq chip design with labeled inlet and outlet holes. Right, comparison of the chip design. The ChronoSeq chip has three key modifications compared to the Drop-seq chip. 1: The Droplet Mixer near the Drop-seq outlet hole has been removed to reduce the likelihood of blockage. 2: The width of the flow-resistors has been increased along with the length of the channels to keep the flow resistance identical between the two designs. 3. The straight (Poisson) ordering inlet has been replaced with an inertial (deterministic) ordering spiral design. These modifications aim to improve the chip's performance in terms of reduced clogging, maintained flow dynamics, and enhanced cell/bead ordering for more efficient single-cell encapsulation. The inertial ordering design, in particular, allows for a more deterministic approach to cell and bead pairing, potentially increasing the capture efficiency of single cells with single beads.

Supplementary Table S1: Cq Values for HPRT1 for K562 cells stimulated THP-1 supernatant and controls: NaN means no Cq value obtained due to lack of amplification for that sample. Results are consistent across both replicates and show addition of THP-1 supernatant leads to RNA degradation.
Gene | Stimulant for K562 cells | K562 cells
| | stimulation duration | Replicate | Cq
HPRT1 | LPS stimulated THP-1 cells
| supernatant taken at 2 hours | 1 hour | 1 | NaN
HPRT1 | LPS stimulated THP-1 cells
| supernatant taken at 2 hours | 1 hour | 2 | NaN
HPRT1 | LPS stimulated THP-1 cells
| supernatant taken immediately-0 hours | 1 hour | 1 | NaN
HPRT1 | LPS stimulated THP-1 cells
| supernatant taken immediately-0 hours | 1 hour | 2 | NaN
HPRT1 | Cell culture media DMEM- No
| stimulation | 1 hour | 1 | 32.48
HPRT1 | Cell culture media DMEM-No
| stimulation | 1 hour | 2 | 32.29
HPRT1 | 10ng/ml TNF-α | 1 hour | 1 | 31.88
HPRT1 | 10ng/ml TNF-α | 1 hour | 2 | 31.68
HPRT1 | Blank Control no K562 cells only water | N/A | 1 | NaN
HPRT1 | Blank Control no K562 cells only water | N/A | 2 | NaN

REFERENCES
1. Bunne, C. et al. How to build the virtual cell with artificial intelligence: Priorities and

opportunities. Cell 187, 7045–7063 (2024).

2. Roohani, Y. H. et al. Virtual Cell Challenge: Toward a Turing test for the virtual cell. Cell

188, 3370–3374 (2025).

3. Hafner, A. et al. p53 pulses lead to distinct patterns of gene expression albeit similar DNA-

binding dynamics. Nat. Struct. Mol. Biol. 24, 840–847 (2017).

4. Zambrano, S., De Toma, I., Piffer, A., Bianchi, M. E. & Agresti, A. NF-κB oscillations

translate into functionally related patterns of gene expression. eLife 5, e09100 (2016).

5. Lane, K. et al. Measuring Signaling and RNA-Seq in the Same Cell Links Gene Expression

to Dynamic Patterns of NF-κB Activation. Cell Syst. 4, 458-469.e5 (2017).

6. Chen, W. et al. Live-seq enables temporal transcriptomic recording of single cells. Nature

608, 733–740 (2022).

7. Macosko, E. Z. et al. Highly Parallel Genome-wide Expression Profiling of Individual Cells

Using Nanoliter Droplets. Cell 161, 1202–1214 (2015).

8. Klein, A. M. et al. Droplet Barcoding for Single-Cell Transcriptomics Applied to Embryonic

Stem Cells. Cell 161, 1187–1201 (2015).

9. Han, X. et al. Mapping the Mouse Cell Atlas by Microwell-Seq. Cell 172, 1091-1107.e17

(2018).

10. Shalek, A. K. et al. Single-cell RNA-seq reveals dynamic paracrine control of cellular

variation. Nature 510, 363–369 (2014).

11. Zheng, G. X. Y. et al. Massively parallel digital transcriptional profiling of single cells. Nat.

Commun. 8, 14049 (2017).

12. Rosenberg, A. B. et al. Single-cell profiling of the developing mouse brain and spinal cord

with split-pool barcoding. Science 360, 176–182 (2018).

13. Lake, B. B. et al. Neuronal subtypes and diversity revealed by single-nucleus RNA

sequencing of the human brain. Science 352, 1586–1590 (2016).

14. Clark, I. C. et al. Microfluidics-Free Single-Cell Genomics with Templated Emulsification.

(2022) doi:10.1101/2022.06.10.495582.

15. Love, J. C., Gierahn, T. M., Shalek, A. K., Wadsworth, M. H. & Hughes, T. K. Single cell

analyses. (2024).

16. Gierahn, T. M. et al. Seq-Well: portable, low-cost RNA sequencing of single cells at high

throughput. Nat. Methods 14, 395–398 (2017).

17. Tay, S. et al. Single-cell NF-κB dynamics reveal digital activation and analogue information

processing. Nature 466, 267–271 (2010).

18. Qiu, Q. et al. Massively parallel and time-resolved RNA sequencing in single cells with

scNT-seq. Nat. Methods 17, 991–1001 (2020).

19. Davari, K. et al. Rapid Genome-wide Recruitment of RNA Polymerase II Drives

Transcription, Splicing, and Translation Events during T Cell Responses. Cell Rep. 19, 643–

654 (2017).

20. Erhard, F. et al. scSLAM-seq reveals core features of transcription dynamics in single cells.

Nature 571, 419–423 (2019).

21. Battich, N. et al. Sequencing metabolically labeled transcripts in single cells reveals mRNA

turnover strategies. Science 367, 1151–1156 (2020).

22. Erhard, F. et al. Time-resolved single-cell RNA-seq using metabolic RNA labelling. Nat.

Rev. Methods Primer 2, 1–18 (2022).

23. Liu, H. et al. SLAM‐Drop‐seq reveals mRNA kinetic rates throughout the cell cycle. Mol.

Syst. Biol. 19, e11427 (2023).

24. Mahat, D. B. et al. Single-cell nascent RNA sequencing unveils coordinated global

transcription. Nature 631, 216–223 (2024).

25. Purvis, J. E. & Lahav, G. Encoding and Decoding Cellular Information through Signaling

Dynamics. Cell 152, 945–956 (2013).

26. Gómez-Sjöberg, R., Leyrat, A. A., Pirone, D. M., Chen, C. S. & Quake, S. R. Versatile,

Fully Automated, Microfluidic Cell Culture System. Anal. Chem. 79, 8557–8563 (2007).

27. Kellogg, R. A., Gómez-Sjöberg, R., Leyrat, A. A. & Tay, S. High-throughput microfluidic

single-cell analysis pipeline for studies of signaling dynamics. Nat. Protoc. 9, 1713–1726

(2014).

28. Yang, J.-M. et al. Deciphering cell signaling networks with massively multiplexed biosensor

barcoding. Cell 184, 6193-6206.e14 (2021).

29. Zhao, S. et al. A single-cell massively parallel reporter assay detects cell-type-specific gene

regulation. Nat. Genet. 55, 346–354 (2023).

30. Schiebinger, G. et al. Optimal-Transport Analysis of Single-Cell Gene Expression Identifies

Developmental Trajectories in Reprogramming. Cell 176, 928-943.e22 (2019).

31. Van den Berge, K. et al. Trajectory-based differential expression analysis for single-cell

sequencing data. Nat. Commun. 11, 1201 (2020).

32. Guo, Q. et al. NF-κB in biology and targeted therapy: new insights and translational

implications. Signal Transduct. Target. Ther. 9, 53 (2024).

33. Türei, D. et al. Integrated intra‐ and intercellular signaling knowledge for multicellular omics

analysis. Mol. Syst. Biol. 17, e9923 (2021).

34. Moerman, T. et al. GRNBoost2 and Arboreto: efficient and scalable inference of gene

regulatory networks. Bioinforma. Oxf. Engl. 35, 2159–2161 (2019).

35. Kim, S. ppcor: An R Package for a Fast Calculation to Semi-partial Correlation Coefficients.

Commun. Stat. Appl. Methods 22, 665–674 (2015).

36. Papili Gao, N., Ud-Dean, S. M. M., Gandrillon, O. & Gunawan, R. SINCERITIES: inferring

gene regulatory networks from time-stamped single cell transcriptional expression profiles.

Bioinforma. Oxf. Engl. 34, 258–266 (2018).

37. Huynh-Thu, V. A., Irrthum, A., Wehenkel, L. & Geurts, P. Inferring Regulatory Networks

from Expression Data Using Tree-Based Methods. PLOS ONE 5, e12776 (2010).

38. Dunham, I. et al. An integrated encyclopedia of DNA elements in the human genome.

Nature 489, 57–74 (2012).

39. Chevalley, M., Roohani, Y. H., Mehrjou, A., Leskovec, J. & Schwab, P. A large-scale

benchmark for network inference from single-cell perturbation data. Commun. Biol. 8, 412

(2025).

40. Han, H. et al. TRRUST v2: an expanded reference database of human and mouse

transcriptional regulatory interactions. https://dx.doi.org/10.1093/nar/gkx1013.

41. Perik-Zavodskaia, O. et al. Knockouts of TNFRSF1A and TNFRSF1B Genes in K562 Cell

Line Lead to Diverse Long-Lasting Responses to TNF-α. Int. J. Mol. Sci. 24, 17169 (2023).

42. Takashiba, S. et al. Differentiation of Monocytes to Macrophages Primes Cells for

Lipopolysaccharide Stimulation via Accumulation of Cytoplasmic Nuclear Factor κB. Infect.

Immun. 67, 5573–5578 (1999).

43. Caldwell, A. B., Cheng, Z., Vargas, J. D., Birnbaum, H. A. & Hoffmann, A. Network

dynamics determine the autocrine and paracrine signaling functions of TNF. Genes Dev. 28,

2120–2133 (2014).

44. Jin, S. et al. Inference and analysis of cell-cell communication using CellChat. Nat.

Commun. 12, 1088 (2021).

45. Granger, C. W. J. Investigating Causal Relations by Econometric Models and Cross-spectral

Methods. Econometrica 37, 424–438 (1969).

46. Ubanako, P., Xelwa, N. & Ntwasa, M. LPS induces inflammatory chemokines via TLR-4

signalling and enhances the Warburg Effect in THP-1 cells. PloS One 14, e0222614 (2019).

47. Wan, J. et al. NF-κB inhibition attenuates LPS-induced TLR4 activation in monocyte cells.

Mol. Med. Rep. 14, 4505–4510 (2016).

48. Mazutis, L. et al. Single-cell analysis and sorting using droplet-based microfluidics. Nat.

Protoc. 8, 870–891 (2013).

49. Wolf, F. A., Angerer, P. & Theis, F. J. SCANPY: large-scale single-cell gene expression data

analysis. Genome Biol. 19, 15 (2018).

50. Wolock, S. L., Lopez, R. & Klein, A. M. Scrublet: Computational Identification of Cell

Doublets in Single-Cell Transcriptomic Data. Cell Syst. 8, 281-291.e9 (2019).

51. Kowalczyk, M. S. et al. Single-cell RNA-seq reveals changes in cell cycle and differentiation

programs upon aging of hematopoietic stem cells. Genome Res. 25, 1860–1872 (2015).

52. Zhang, Y., Parmigiani, G. & Johnson, W. E. ComBat-seq: batch effect adjustment for RNA-

seq count data. NAR Genomics Bioinforma. 2, lqaa078 (2020).

53. Sheu, K. M., Pimplaskar, A. & Hoffmann, A. Single-cell stimulus-response gene expression

trajectories reveal the stimulus specificities of dynamic responses by single macrophages.

Mol. Cell 84, 4095-4110.e6 (2024).

54. Lange, M. et al. CellRank for directed single-cell fate mapping. Nat. Methods 19, 159–170

(2022).

55. Livak, K. J. & Schmittgen, T. D. Analysis of relative gene expression data using real-time

quantitative PCR and the 2(-Delta Delta C(T)) Method. Methods San Diego Calif 25, 402–

408 (2001).

56. Ciubotaru, I., Potempa, L. A. & Wander, R. C. Production of modified C-reactive protein in

U937-derived macrophages. Exp. Biol. Med. Maywood NJ 230, 762–770 (2005).

57. Ward, T., Faivre, M., Abkarian, M. & Stone, H. A. Microfluidic flow focusing: Drop size

and scaling in pressure versus flow-rate-driven pumping. ELECTROPHORESIS 26, 3716–

3724 (2005).

58. Moon, H.-S. et al. Inertial-ordering-assisted droplet microfluidics for high-throughput single-

cell RNA-sequencing. Lab. Chip 18, 775–784 (2018).

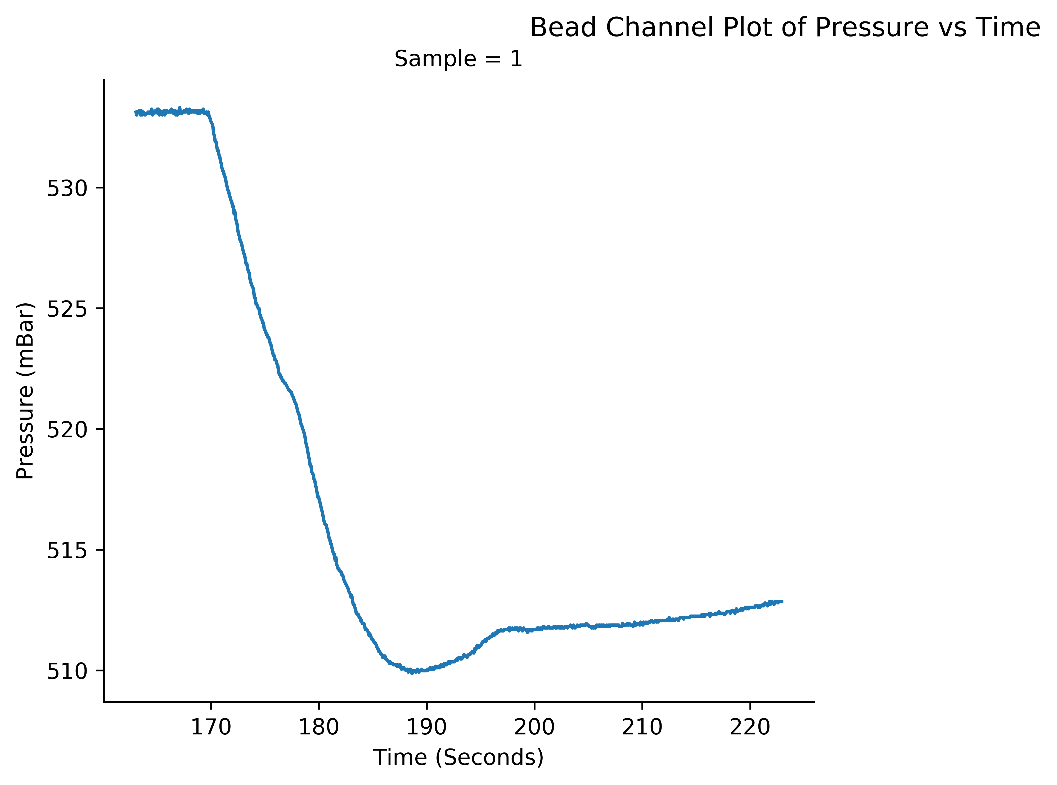
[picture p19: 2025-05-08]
BeadPressure.png

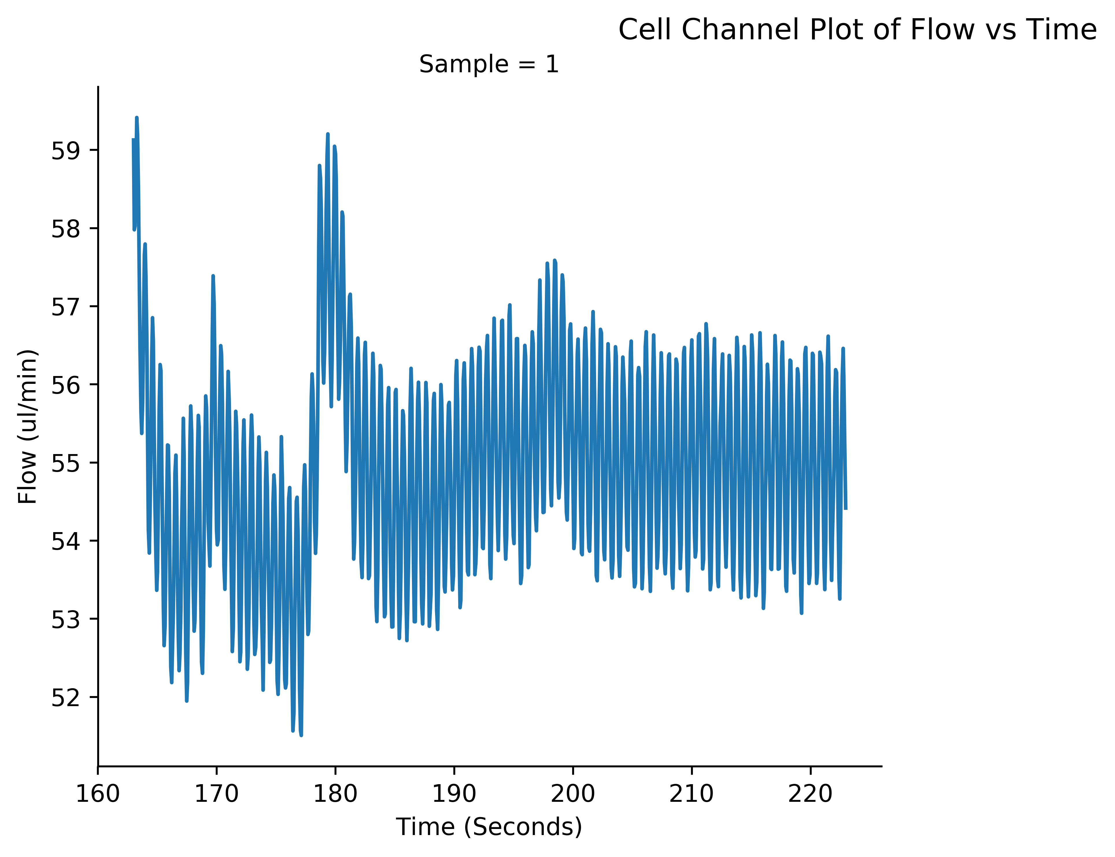
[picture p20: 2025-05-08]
CellFlow.png

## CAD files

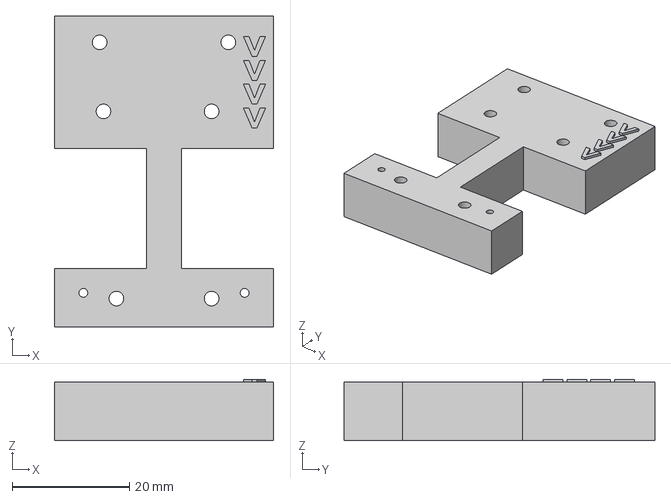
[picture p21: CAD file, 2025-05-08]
CAD_Files/XYZ Robot/XYZ Robot Servo Bracket Mount Assembly v25 Mouting Plate.step
37.5 x 53.1 x 10.5 mm

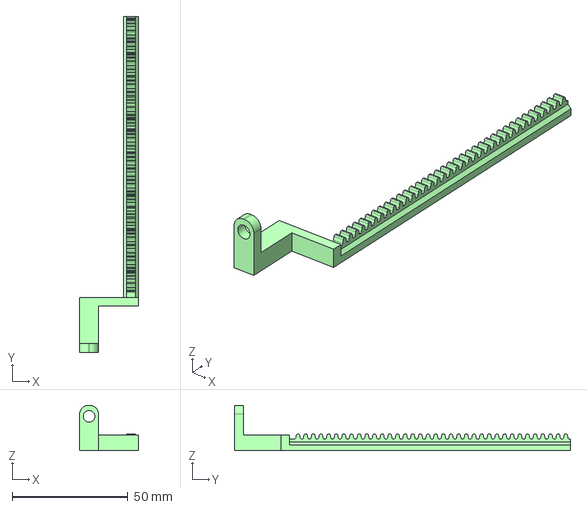
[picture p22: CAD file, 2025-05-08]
CAD_Files/XYZ Robot/XYZ Robot Servo Bracket Mount Assembly v22 Pusher.step
25.4 x 145.0 x 19.6 mm

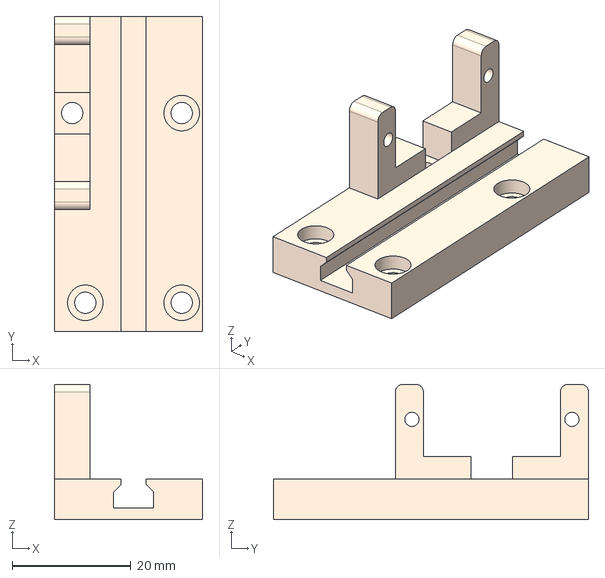
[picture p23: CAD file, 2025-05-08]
CAD_Files/XYZ Robot/XYZ Robot Servo Bracket Mount Assembly v22 Bracket.step
25.0 x 53.2 x 22.8 mm

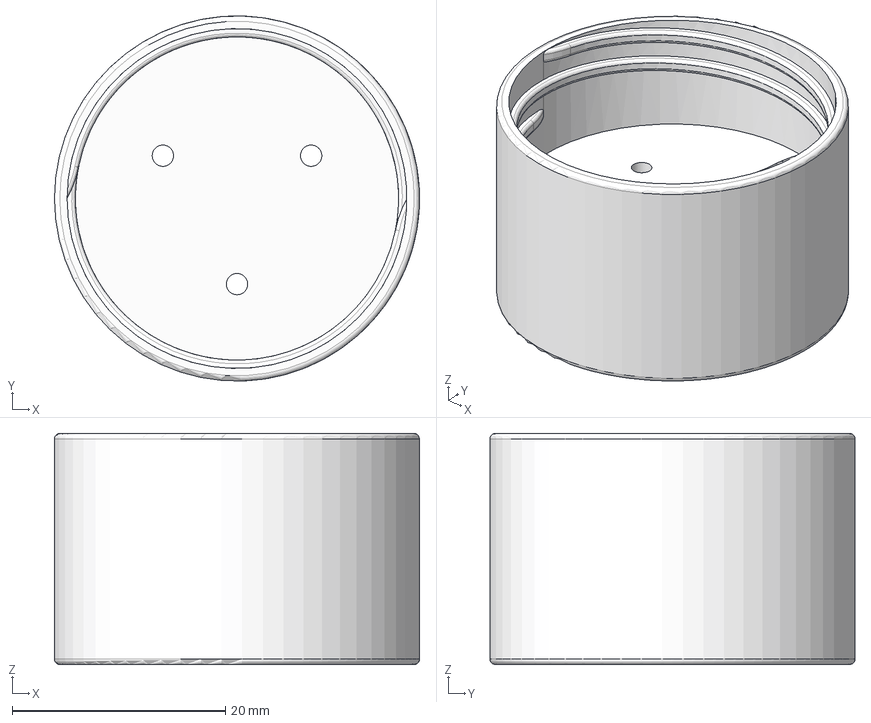
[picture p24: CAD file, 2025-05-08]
CAD_Files/3 Port Reservoir/50ML FALCON CAP 3 PORT v12.step
34.2 x 34.2 x 21.7 mm

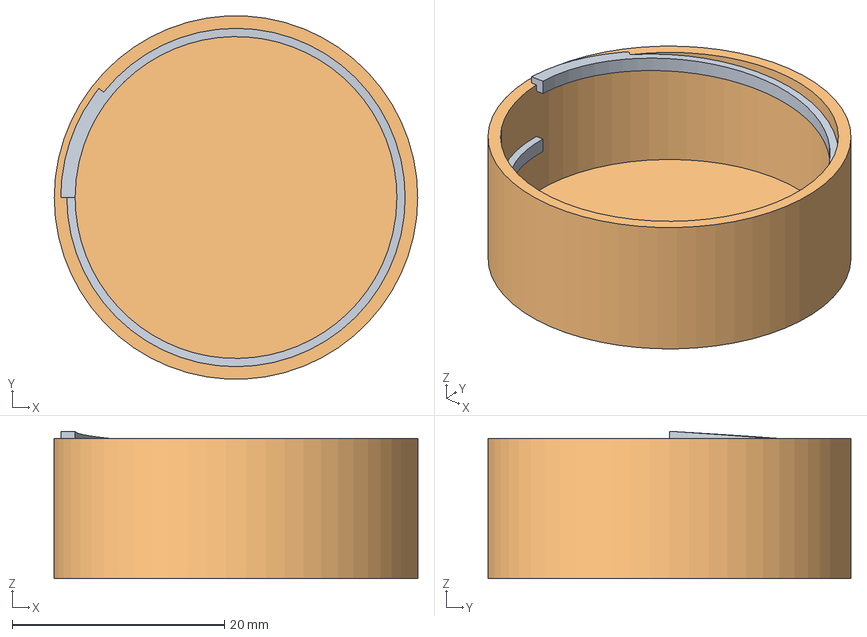
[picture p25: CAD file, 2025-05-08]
CAD_Files/3 Port Reservoir/Intermediate Files/50ML FALCON CAP 3 PORT Single Coil Intermediate.step
34.2 x 34.2 x 13.9 mm

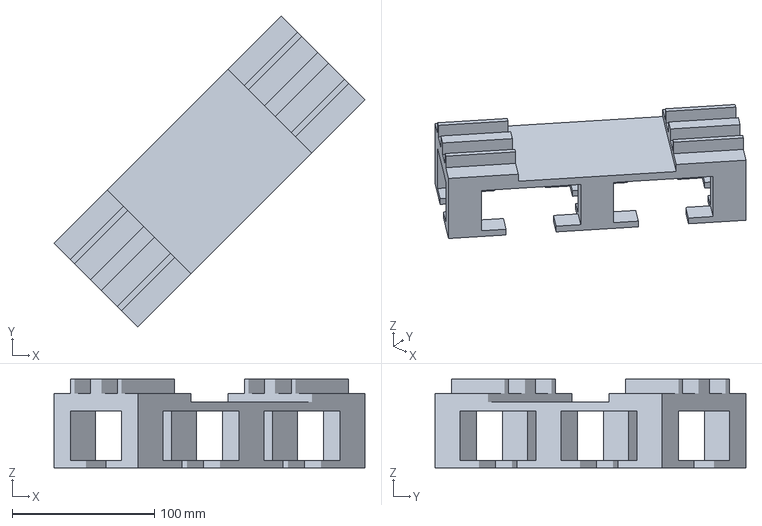
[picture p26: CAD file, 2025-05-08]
CAD_Files/ChronoSeq Device/cell and oil channel flow sensors holder/cell_and_oil_flow_sensor_fused_holder.3mf
218.9 x 218.9 x 62.3 mm

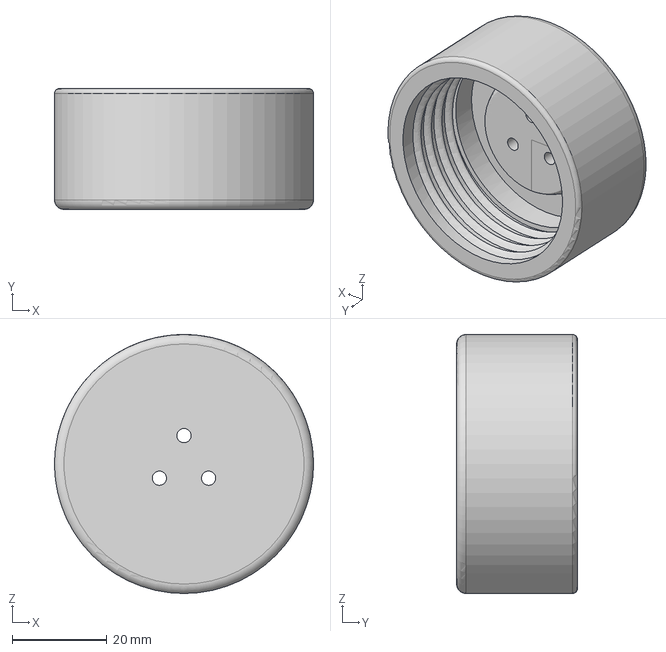
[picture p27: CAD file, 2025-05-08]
CAD_Files/ChronoSeq Device/GL45 Cap for Bleach Bottle/GL45 CAP flat top for bleach bottle.step
54.7 x 25.5 x 54.7 mm

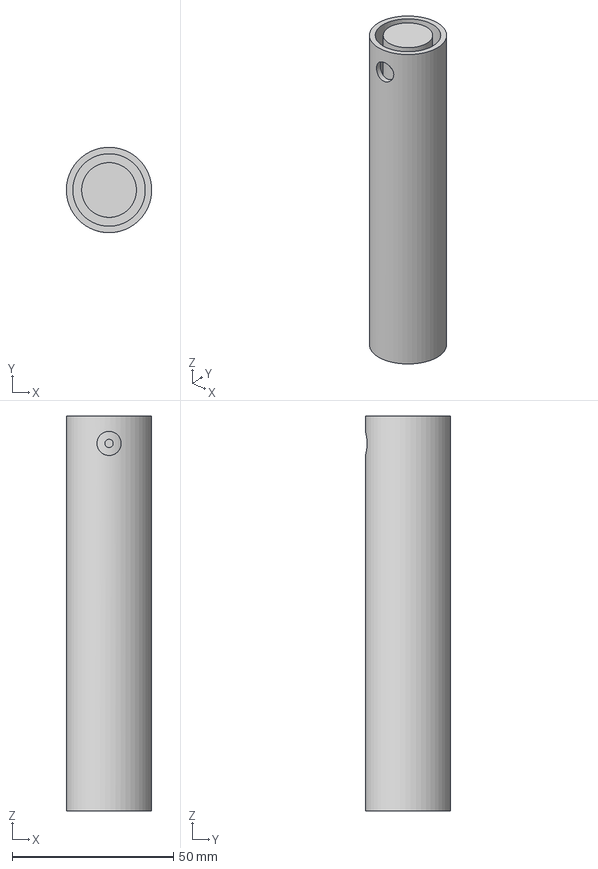
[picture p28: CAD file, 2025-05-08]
CAD_Files/ChronoSeq Device/HUANO Monitor Riser legs extension. Shorter/Computer Monitor Riser HUANO legs extension. Shorter v2.step
26.5 x 26.5 x 122.5 mm

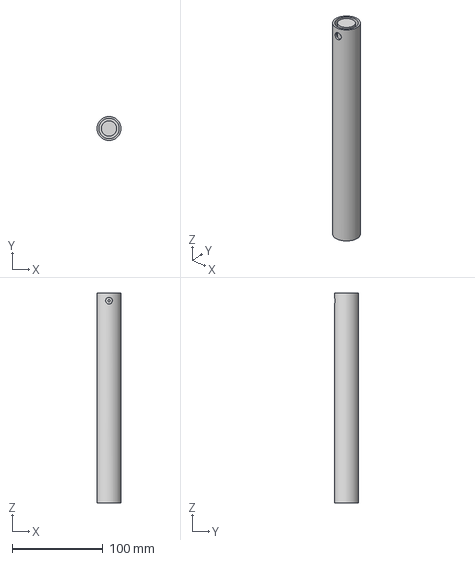
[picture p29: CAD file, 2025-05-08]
CAD_Files/ChronoSeq Device/HUANO Monitor Riser legs extension. Taller/Computer Monitor Riser HUANO legs extension. Taller v16.step
26.5 x 26.5 x 231.4 mm

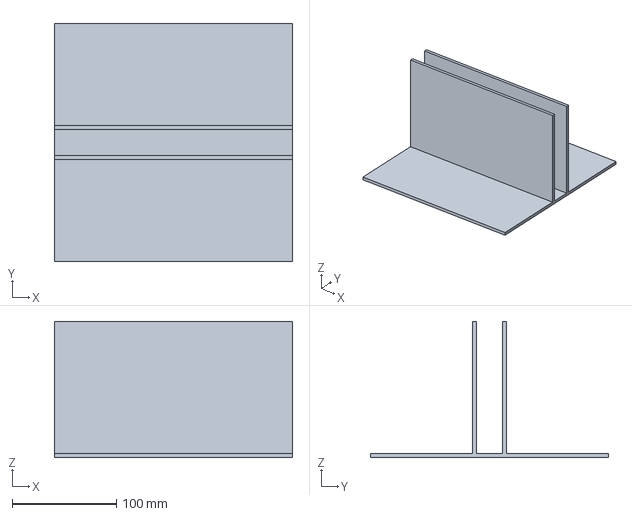
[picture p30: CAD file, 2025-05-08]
CAD_Files/ChronoSeq Device/Laptop Vertical Holder/Laptop Vertical Holder.3mf
228.6 x 228.6 x 131.0 mm

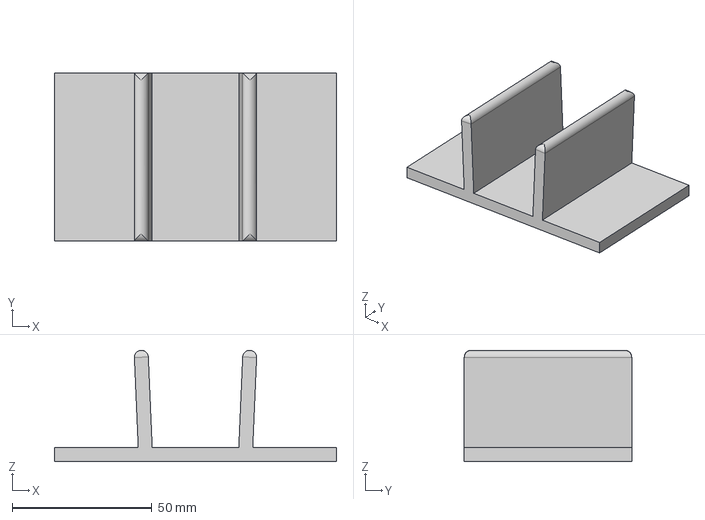
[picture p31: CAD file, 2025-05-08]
CAD_Files/ChronoSeq Device/Pipette Holder Below LPS or TNFalpha addition/Pipette_Holder_before_LPS_injection v1.step
101.0 x 60.0 x 39.9 mm

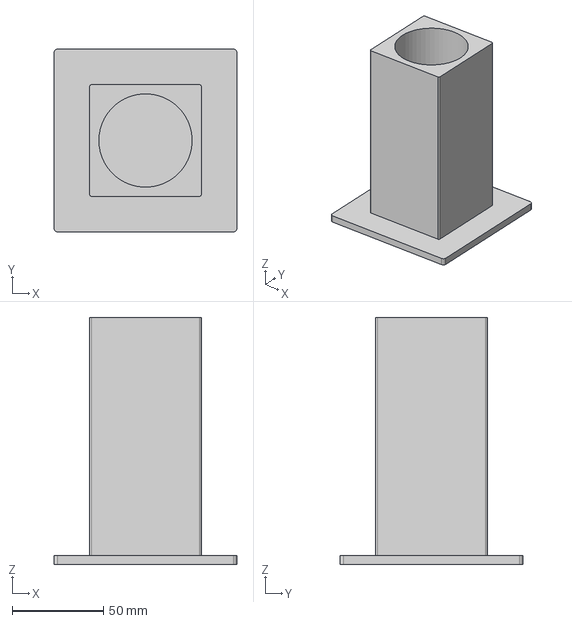
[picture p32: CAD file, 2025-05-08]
CAD_Files/ChronoSeq Device/Wilkerson M18-02-BK00B Filter Holder/Wilkerson M18-02-BK00B Filter Holder v1.step
100.0 x 100.0 x 135.0 mm

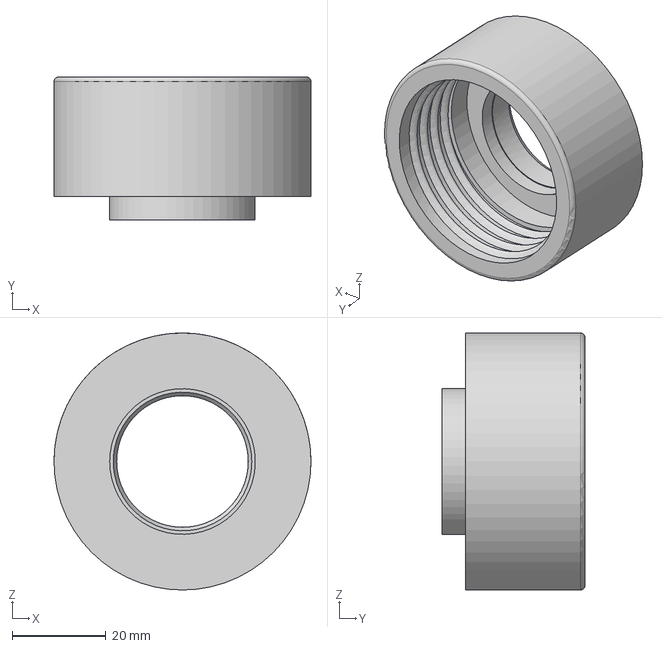
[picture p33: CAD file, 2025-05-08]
CAD_Files/GL45_CAP/GL45 CAP with Pluriselect Connector Ring Slot v4.step
54.7 x 30.5 x 54.7 mm

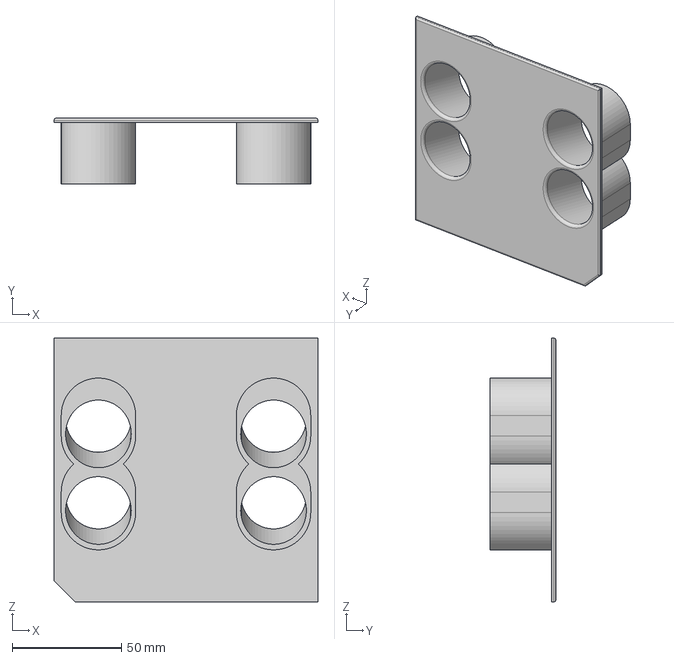
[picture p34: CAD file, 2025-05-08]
CAD_Files/Ice Box Lids for Heathrow Scientific HS23271A/50ml AutoCAD sketch import no middle v18.step
120.6 x 30.0 x 120.6 mm

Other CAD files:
CAD_Files/iPhone 13 Pro Holder and Lens Attachment for Recording on the Motic AE31 Microscope/iPhone 13 Pro AE31 Lens Mount .3mf
CAD_Files/Microfluidic Chip Manufacture/2D CAD Model for Chip/HighResistanceWideChannelV14.dwg
CAD_Files/Microfluidic Chip Manufacture/3D CAD Models/Wafer Loader 1.step
CAD_Files/3 Port Reservoir/3 Port Cap XY Compensation.3mf
CAD_Files/3 Port Reservoir/50ML FALCON CAP 3 PORT v12.f3d
CAD_Files/3 Port Reservoir/Intermediate Files/50ML FALCON CAP 3 PORT v12 Two Coils Intermediate File.step
CAD_Files/ChronoSeq Device/50ml conical tube holder/50ml Holder with Wide Base.3mf
CAD_Files/ChronoSeq Device/GL45 Cap for Bleach Bottle/GL45 CAP flat top for bleach bottle.3mf
CAD_Files/ChronoSeq Device/GL45 Cap for Bleach Bottle/GL45 CAP flat top for bleach bottle.f3d
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

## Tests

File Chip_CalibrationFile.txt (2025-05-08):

257.2170543682807
414.19356535171386
769.3665765181726
55.08801332401252
55.48109254967183
200.19608167485706

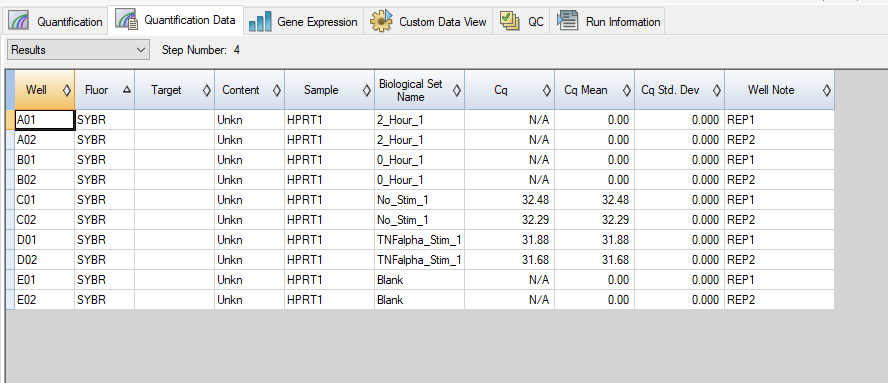
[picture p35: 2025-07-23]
qPCR_validation_files/K562_Costimulation_2_Samples/HPRT1 Only/Capture_HPRT1.PNG

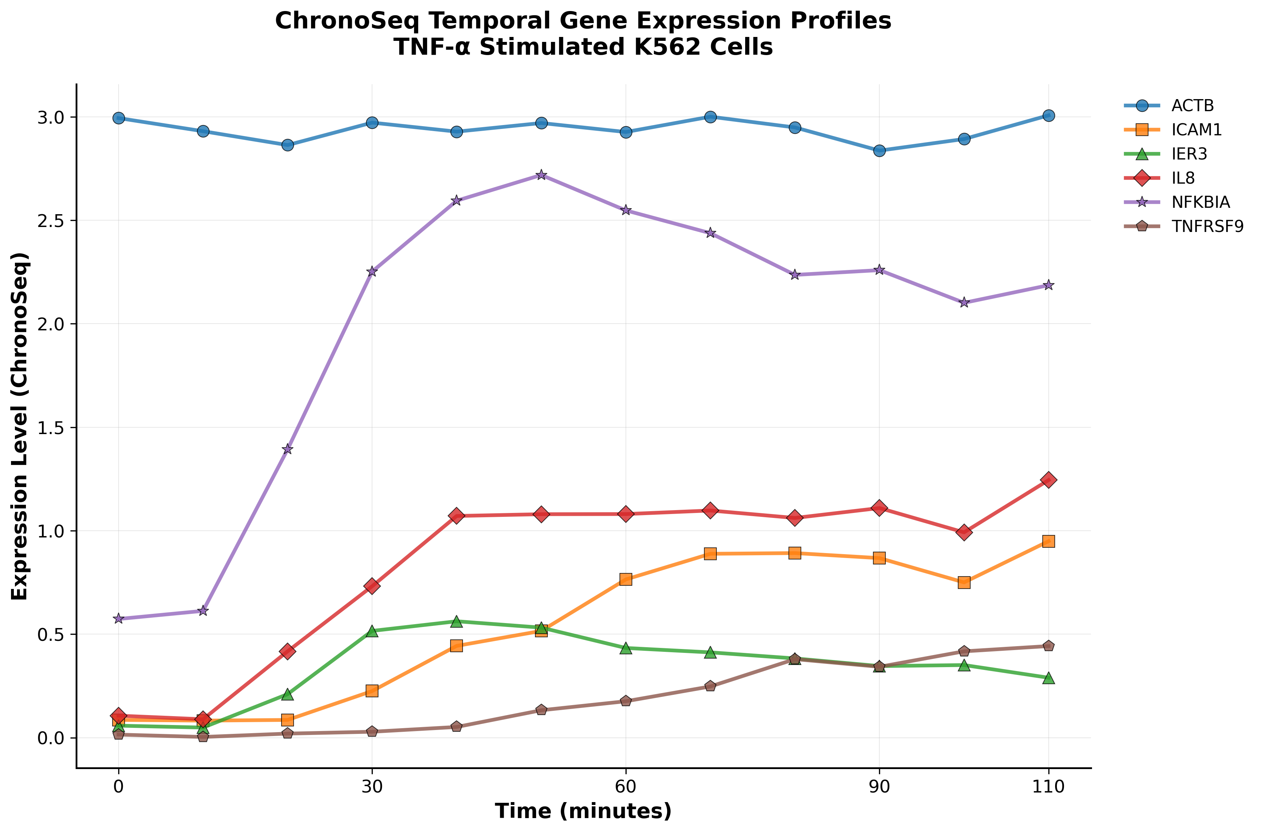
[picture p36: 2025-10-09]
qPCR_validation_files/chronoseq_timeseries.png

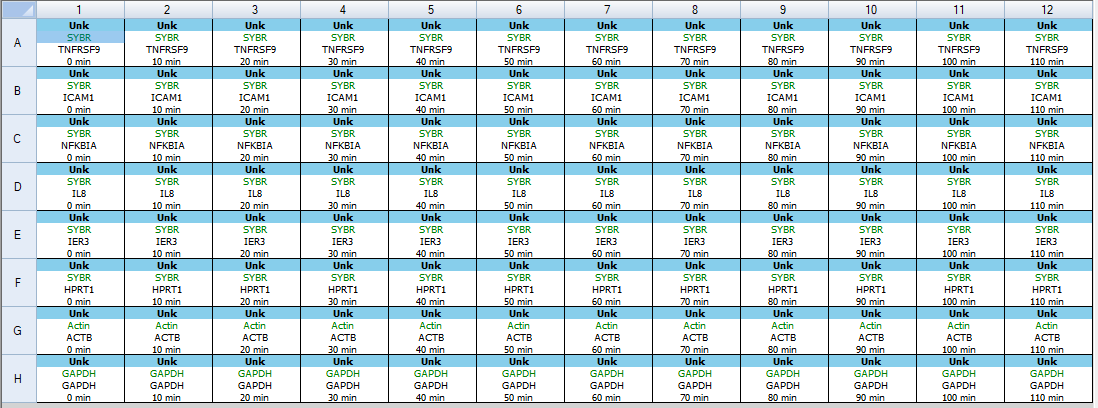
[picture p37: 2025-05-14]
qPCR_validation_files/Plate Structure for Validation.PNG

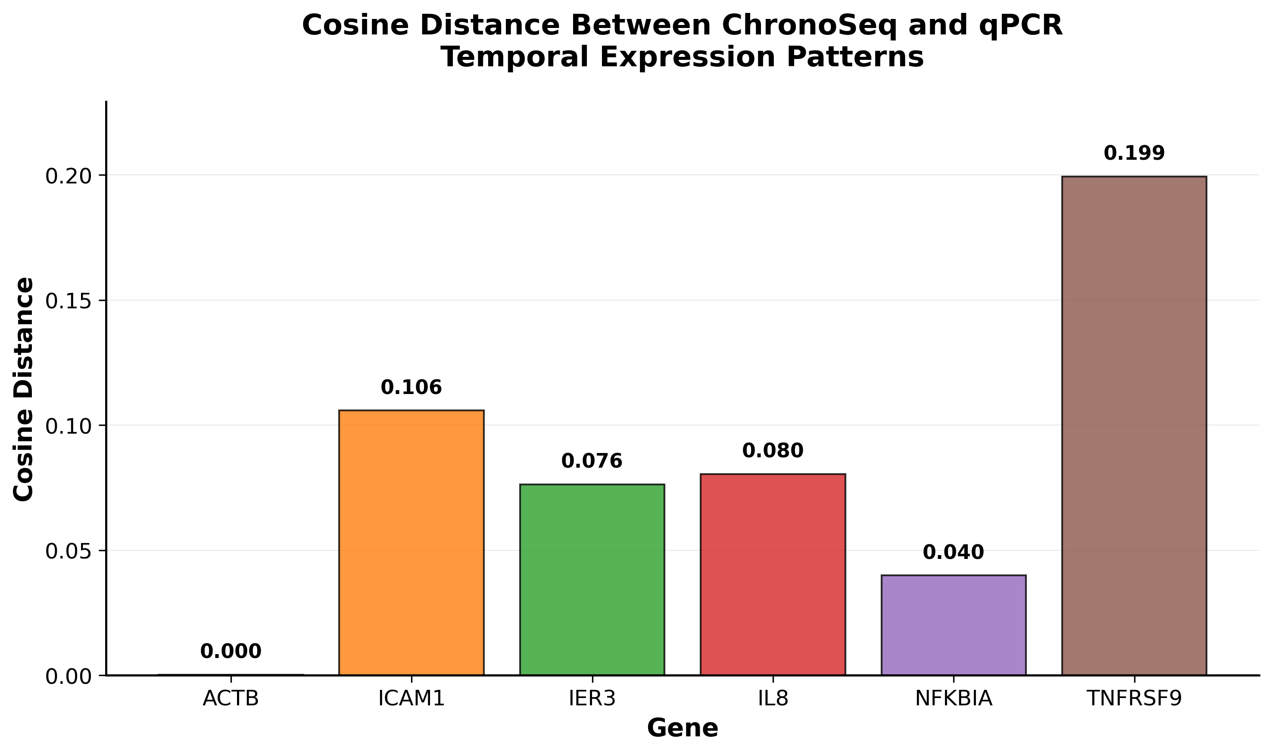
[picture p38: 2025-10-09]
qPCR_validation_files/cosine_distance_bar_chart.png

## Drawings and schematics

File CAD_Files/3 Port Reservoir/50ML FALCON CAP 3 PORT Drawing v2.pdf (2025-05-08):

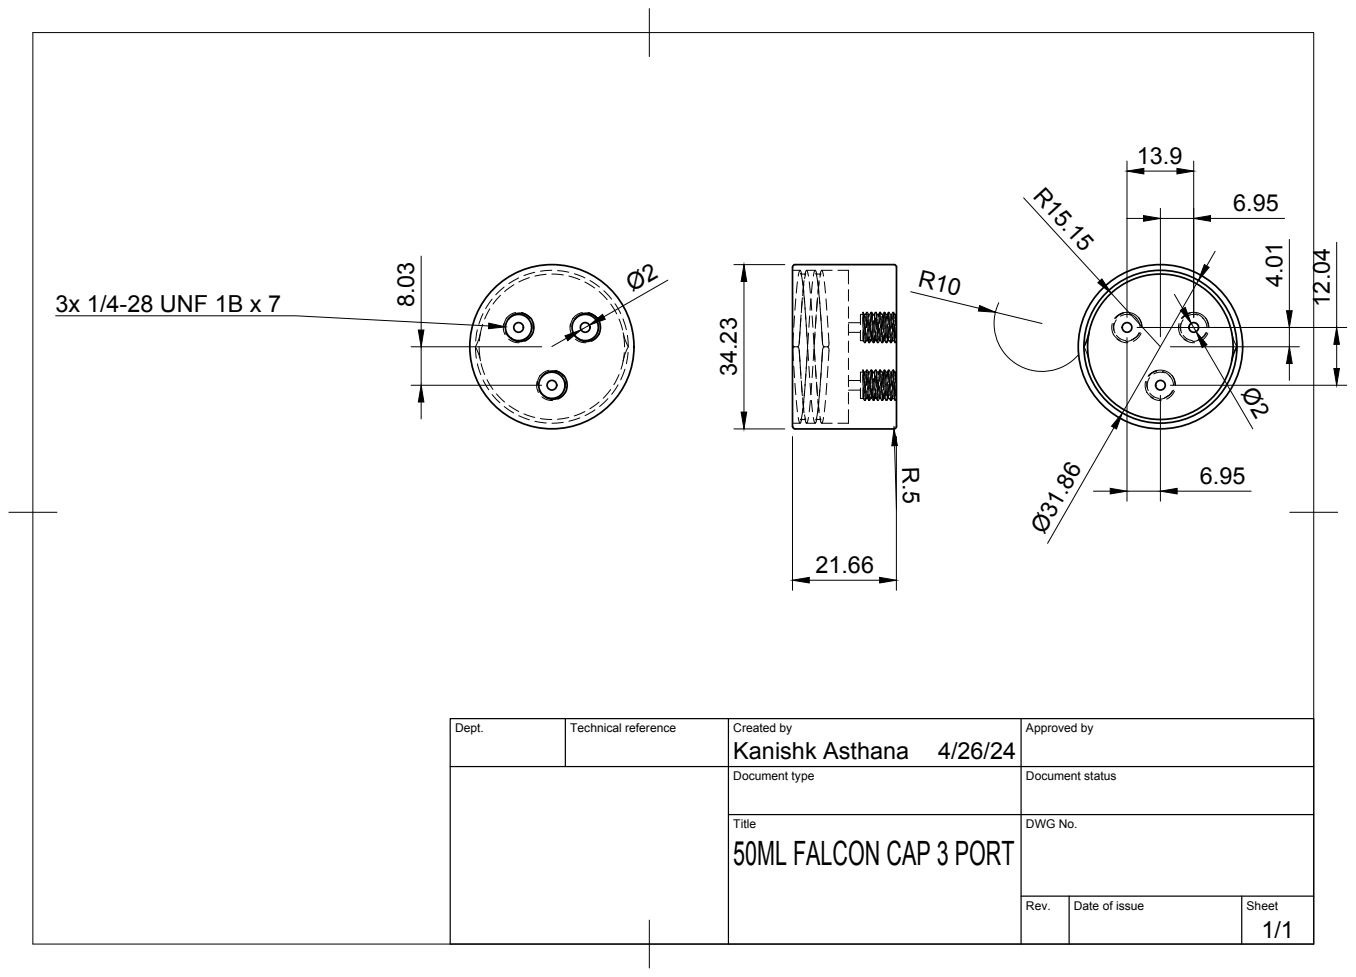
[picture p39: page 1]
Kanishk Asthana 34.23; 3x 1/4-28 UNF 1B x 7

Dept. | Technical reference | Created by 4/26/24 | Approved by

Document type | Document status

Title 50ML FALCON CAP 3 PORT | DWG No.

Rev. | Date of issue | Sheet 1/1

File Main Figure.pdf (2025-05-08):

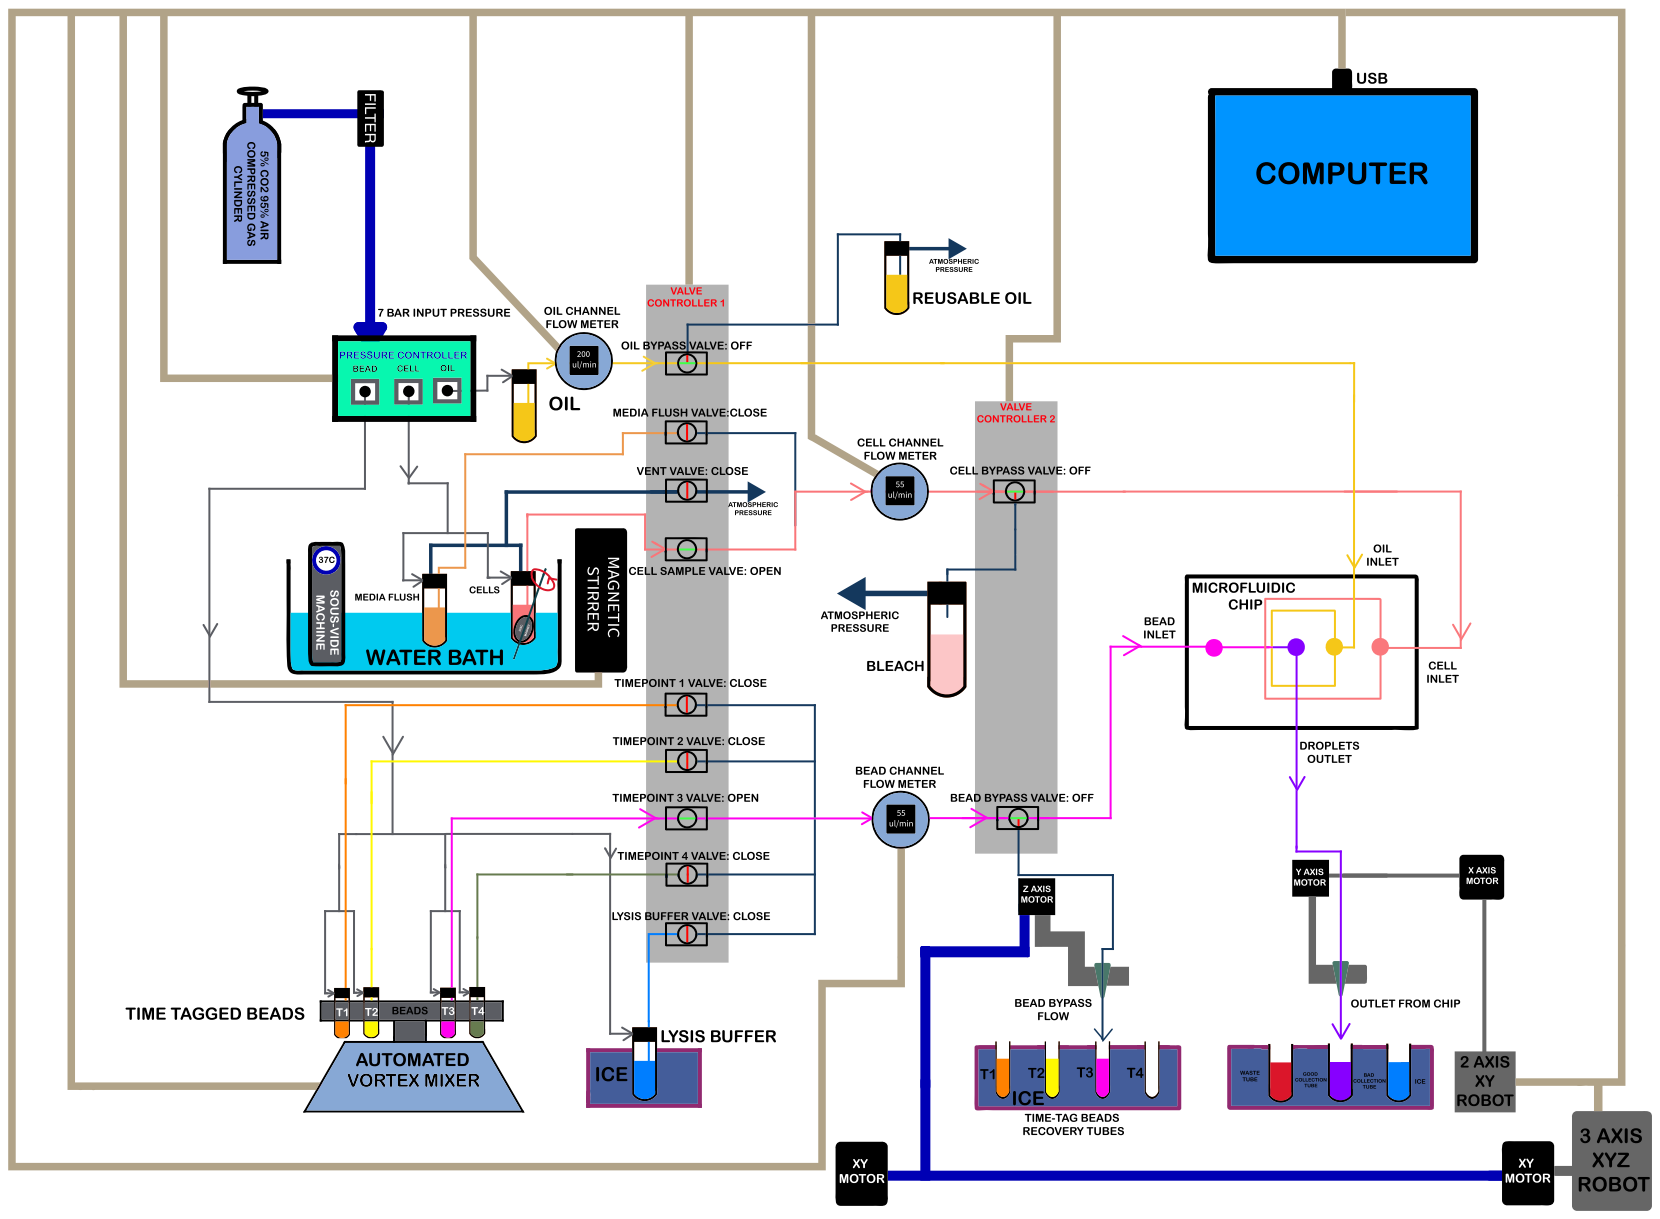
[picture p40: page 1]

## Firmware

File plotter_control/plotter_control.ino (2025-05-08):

#include <Servo.h>

#define yAxisLimitPin A0
#define xAxisLimitPin A1
const int servoPin=11;
const int tubeDownAngle=0;
const int tubeUpAngle=180;
const int dirPin2=6;
const int stepPin1=3;
const int stepPin2=2;
const int dirPin1=5;
const int enablePin=8;
int xpos=0;
int ypos=0;
int microDelay=50;
int smoothMotionMicroDelay=100;
int xcount=0;
int ycount=0;
Servo servo1;

void setup() {
  pinMode(yAxisLimitPin,INPUT);
  pinMode(xAxisLimitPin,INPUT);
  pinMode(stepPin1,OUTPUT);
  pinMode(stepPin2,OUTPUT);
  pinMode(dirPin1,OUTPUT);
  pinMode(dirPin2,OUTPUT);
  pinMode(enablePin,OUTPUT);
  Serial.begin(9600);
  servo1.attach(servoPin);
  servo1.write(tubeDownAngle);
  digitalWrite(enablePin,HIGH);//Disable Motor on Startup
}

void enableMotors(){
  digitalWrite(enablePin,LOW);
}

void disableMotors(){
  digitalWrite(enablePin,HIGH);
}

void moveX(int steps){
  if(xpos+steps>=-12000 && xpos+steps<=0){
    xpos=xpos+steps;
    if(steps>0){
      digitalWrite(dirPin1,HIGH);
      digitalWrite(dirPin2,HIGH);
    }
    else{
      digitalWrite(dirPin1,LOW);
      digitalWrite(dirPin2,LOW);
    }
    
    for(int i=0;i<abs(steps);i++){
      digitalWrite(stepPin1,HIGH);
      digitalWrite(stepPin2,HIGH);
      delayMicroseconds(microDelay);
      digitalWrite(stepPin1,LOW);
      digitalWrite(stepPin2,LOW);
      delayMicroseconds(microDelay);
    }
  }
  else{
     Serial.println("Error!That position is out of bounds! I Cannot move there.");
    }
}

void moveY(int steps){
  if(ypos+steps>=-20000 && ypos+steps<=0){
    ypos=ypos+steps;
    if(steps>0){
      digitalWrite(dirPin1,HIGH);
      digitalWrite(dirPin2,LOW);
    }
    else{
      digitalWrite(dirPin1,LOW);
      digitalWrite(dirPin2,HIGH);
    }
    
    for(int i=0;i<abs(steps);i++){
      digitalWrite(stepPin1,HIGH);
      digitalWrite(stepPin2,HIGH);
      delayMicroseconds(microDelay);
      digitalWrite(stepPin1,LOW);
      digitalWrite(stepPin2,LOW);
      delayMicroseconds(microDelay);
    }
  }
  else{
    Serial.println("Error!That position is out of bounds! I Cannot move there.");
  }
}

void moveYSmoothly(int steps){
  if(ypos+steps>=-20000 && ypos+steps<=0){
    ypos=ypos+steps;
    if(steps>0){
      digitalWrite(dirPin1,HIGH);
      digitalWrite(dirPin2,LOW);
    }
    else{
      digitalWrite(dirPin1,LOW);
      digitalWrite(dirPin2,HIGH);
    }
    int startDelay=500+smoothMotionMicroDelay,stopDelay=smoothMotionMicroDelay;
    for(int i=0;i<abs(steps);i++){
      if(i<500){
        digitalWrite(stepPin1,HIGH);
        digitalWrite(stepPin2,HIGH);
        delayMicroseconds(startDelay);
        digitalWrite(stepPin1,LOW);
        digitalWrite(stepPin2,LOW);
        delayMicroseconds(startDelay);
        startDelay--;
      }
      else if(i>=500 && i<(abs(steps)-500)){
        digitalWrite(stepPin1,HIGH);
        digitalWrite(stepPin2,HIGH);
        delayMicroseconds(smoothMotionMicroDelay);
        digitalWrite(stepPin1,LOW);
        digitalWrite(stepPin2,LOW);
        delayMicroseconds(smoothMotionMicroDelay);
      }
      else if(i>=(abs(steps)-500)){
        digitalWrite(stepPin1,HIGH);
        digitalWrite(stepPin2,HIGH);
        delayMicroseconds(stopDelay);
        digitalWrite(stepPin1,LOW);
        digitalWrite(stepPin2,LOW);
        delayMicroseconds(stopDelay);
        stopDelay++;
      }
      
    }
  }
  else{
    Serial.println("Error!That position is out of bounds! I Cannot move there.");
  }
}

void tubeControl(int command){
  if(command==1){
    servo1.write(tubeUpAngle);
  }
  else{
    servo1.write(tubeDownAngle);
  }
  delay(500);
}

void tubeControlFast(int command){
  if(command==1){
    servo1.write(tubeUpAngle);
  }
  else{
    servo1.write(tubeDownAngle);
  }
  delay(200);
}

void tubeDownSmoothly(){
  int initialPosition=2400;//Always call this function with the previous position having tube up. Otherwise it defeats the purpose of smooth motion.
  int finalPosition=544;
  for(int i=initialPosition;i>=finalPosition;i--){
    servo1.writeMicroseconds(i);
    if(i>=2200 && i<=2400)
      delayMicroseconds(2000);
    else if(i>=2000 && i<2200)
      delayMicroseconds(1000);
    else if(i>=944 && i<2000)
      delayMicroseconds(500);
    else if(i>=744 && i<944)
      delayMicroseconds(1000);
    else if(i>=544 && i<744)
      delayMicroseconds(2000);
  }
}

//Help recalibrate the robot to keep precision
void goHome(){
 enableMotors();
 tubeControl(1); //Tube Up
 //Moving in Positive Y direction back to Home
 digitalWrite(dirPin1,HIGH);
 digitalWrite(dirPin2,LOW);
 //Keep moving towards the origin till you hit the Y limit switch
 while(digitalRead(yAxisLimitPin)==HIGH){
      digitalWrite(stepPin1,HIGH);
      digitalWrite(stepPin2,HIGH);
      delayMicroseconds(microDelay);
      digitalWrite(stepPin1,LOW);
      digitalWrite(stepPin2,LOW);
      delayMicroseconds(microDelay);
 }
 ypos=0;//Recalibrate
 Serial.println("Y axis recalibrated! We are now at Y=0.");
 
 //Moving in Positive X direction back to Home
 digitalWrite(dirPin1,HIGH);
 digitalWrite(dirPin2,HIGH);
 //Keep moving towards the origin till you hit the X limit switch
 while(digitalRead(xAxisLimitPin)==HIGH){
      digitalWrite(stepPin1,HIGH);
      digitalWrite(stepPin2,HIGH);
      delayMicroseconds(microDelay);
      digitalWrite(stepPin1,LOW);
      digitalWrite(stepPin2,LOW);
      delayMicroseconds(microDelay);
 }
 xpos=0; //Recalibrate
 Serial.println("X axis recalibrated! We are now at X=0.");
 tubeControl(0);//Tube Down
}

void getCoordinatesFromPosition(){
 xcount=0;
 ycount=0;
 enableMotors();
 tubeControl(1); //Tube Up
 //Moving in Positive Y direction back to Home
 digitalWrite(dirPin1,HIGH);
 digitalWrite(dirPin2,LOW);
 //Keep moving towards the origin till you hit the Y limit switch
 while(digitalRead(yAxisLimitPin)==HIGH){
      digitalWrite(stepPin1,HIGH);
      digitalWrite(stepPin2,HIGH);
      delayMicroseconds(microDelay);
      digitalWrite(stepPin1,LOW);
      digitalWrite(stepPin2,LOW);
      delayMicroseconds(microDelay);
      ycount--;
 }
 ypos=0;//Recalibrate
 //Serial.println("Y axis recalibrated! We are now at Y=0.");
 
 //Moving in Positive X direction back to Home
 digitalWrite(dirPin1,HIGH);
 digitalWrite(dirPin2,HIGH);
 //Keep moving towards the origin till you hit the X limit switch
 while(digitalRead(xAxisLimitPin)==HIGH){
      digitalWrite(stepPin1,HIGH);
      digitalWrite(stepPin2,HIGH);
      delayMicroseconds(microDelay);
      digitalWrite(stepPin1,LOW);
      digitalWrite(stepPin2,LOW);
      delayMicroseconds(microDelay);
      xcount--;
 }
 xpos=0; //Recalibrate
 Serial.println("X coordinates are: "+String(xcount)+" . Y coordinates are: "+String(ycount));
 tubeControl(0);//Tube Down
}



void goToCoordinates(int x,int y){
  enableMotors();
  tubeControl(1);
  moveY(y-ypos);
  moveX(x-xpos);
  tubeControl(0);
}

void goToCoordinatesKeepTubeUp(int x,int y){
  enableMotors();
  tubeControl(1);
  moveY(y-ypos);
  moveX(x-xpos);
}

void goToCoordinatesSmoothly(int x,int y){
  enableMotors();
  moveYSmoothly(y-ypos);
  tubeDownSmoothly();
}

void goToCoordinatesFast(int x,int y){
  enableMotors();
  tubeControlFast(1);
  moveY(y-ypos);
  moveX(x-xpos);
  tubeControlFast(0);
}

void loop() {
  
  String commandString=Serial.readStringUntil('\n');
  if(commandString.length()>0){
    int index=0;
    String inputString="";
    do{
      index=commandString.indexOf('|');
      if(index==-1){
        inputString=commandString;
        Serial.println("No remaining commands with the following input:");
        Serial.println(inputString);
      }
      else{
        inputString=commandString.substring(0,index);
        commandString=commandString.substring(index+1);
        Serial.println("Input:");
        Serial.println(inputString);
        Serial.println("Remaining Command:");
        Serial.println(commandString);
      }
      char command=inputString.charAt(0);
      switch(command){
        case 'W':
          delay(inputString.substring(1).toInt());
          break;
        case 'T':
          tubeControl(inputString.substring(1).toInt());
          break;
        case 'V':
          tubeDownSmoothly();
          break;
        case 'X':
          moveX(inputString.substring(1).toInt());
          break;
        case 'Y':
          moveY(inputString.substring(1).toInt());
          break;
        case 'E':
          enableMotors();
          break;
        case 'D':
          disableMotors();
          break;
        case 'H':
          goHome();
          break;
        case 'C':
          getCoordinatesFromPosition();
          break;
        case 'G':
          {
            String coordinates=inputString.substring(1);
            int commaIndex=coordinates.indexOf(',');
            if(commaIndex!=-1){
              int x=coordinates.substring(0,commaIndex).toInt();
              int y=coordinates.substring(commaIndex+1).toInt();
              goToCoordinates(x,y);
            }
          }
          break;
        case 'U':
          {
            String coordinates=inputString.substring(1);
            int commaIndex=coordinates.indexOf(',');
            if(commaIndex!=-1){
              int x=coordinates.substring(0,commaIndex).toInt();
              int y=coordinates.substring(commaIndex+1).toInt();
              goToCoordinatesKeepTubeUp(x,y);
            }
          }
          break;
        case 'M':{
          String microseconds=inputString.substring(1);
          servo1.writeMicroseconds(microseconds.toInt());
        }
          break;
        case 'S':
          {
            String coordinates=inputString.substring(1);
            int commaIndex=coordinates.indexOf(',');
            if(commaIndex!=-1){
              int x=coordinates.substring(0,commaIndex).toInt();
              int y=coordinates.substring(commaIndex+1).toInt();
              goToCoordinatesSmoothly(x,y);
            }
          }
          break;          
        case 'F':
          {
            String coordinates=inputString.substring(1);
            int commaIndex=coordinates.indexOf(',');
            if(commaIndex!=-1){
              int x=coordinates.substring(0,commaIndex).toInt();
              int y=coordinates.substring(commaIndex+1).toInt();
              goToCoordinatesFast(x,y);
            }
          }
          break;
          
      }
    }while(index!=-1);
  }
}

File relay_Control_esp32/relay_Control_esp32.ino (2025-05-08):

//Author Kanishk Asthana kasthana@ucsd.edu
//Defining relay variables according to the pins they are connected to
//ESP32 Pin reference: https://lastminuteengineers.com/esp32-pinout-reference/
const int Relay1 = 16; //RX2
const int Relay2 = 17; //TX2 
const int Relay3 = 18; //D18
const int Relay4 = 19; //D19 
const int Relay5 = 27; //D27  
const int Relay6 = 26; //D26 
const int Relay7 = 33; //D33  
const int Relay8 = 32; //D32 
//Relay vector will store current state of the relays
bool relayStateVector[8]={false,false,false,false,false,false,false,false};
String commandString;
void setup()
{
    Serial.begin(9600);
    pinMode(Relay1, OUTPUT);
    pinMode(Relay2, OUTPUT); 
    pinMode(Relay3, OUTPUT); 
    pinMode(Relay4, OUTPUT); 
    pinMode(Relay5, OUTPUT); 
    pinMode(Relay6, OUTPUT); 
    pinMode(Relay7, OUTPUT); 
    pinMode(Relay8, OUTPUT); 
    
    //Turn all Relays Off as soon as you power up
    
    digitalWrite(Relay1,HIGH);
    digitalWrite(Relay2,HIGH);
    digitalWrite(Relay3,HIGH);
    digitalWrite(Relay4,HIGH);
    digitalWrite(Relay5,HIGH);
    digitalWrite(Relay6,HIGH);
    digitalWrite(Relay7,HIGH);
    digitalWrite(Relay8,HIGH);
}

void updateRelayState(bool stateVector[8]){
  //Inversing order of stateVector to match Hardware Layout
  //Taking the inverse of the stateVector because a low signal turns the relay on
    digitalWrite(Relay1,!stateVector[7]);
    digitalWrite(Relay2,!stateVector[6]);
    digitalWrite(Relay3,!stateVector[5]);
    digitalWrite(Relay4,!stateVector[4]);
    digitalWrite(Relay5,!stateVector[3]);
    digitalWrite(Relay6,!stateVector[2]);
    digitalWrite(Relay7,!stateVector[1]);
    digitalWrite(Relay8,!stateVector[0]);
}

void loop()
{
  if(Serial.available()>8){
    commandString=Serial.readStringUntil('\n');
    if(commandString.length()==8){
      for(int i=0;i<8;i++){
        if(commandString[i]=='0')
          relayStateVector[i]=false;
        else if(commandString[i]=='1')
          relayStateVector[i]=true;
      }
      updateRelayState(relayStateVector);
    }
  }
}
 

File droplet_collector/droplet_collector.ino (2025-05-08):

#include <Servo.h>

const int servoPin2=9;
const int servoPin=11;
int defaultAngle=0;
int angle=defaultAngle;
int angle2=defaultAngle;

Servo servo1;
Servo servo2;
void setup() {
  Serial.begin(9600);
  servo1.attach(servoPin);
  servo1.write(defaultAngle);
  servo2.attach(servoPin2);
  servo2.write(defaultAngle);
}

void setAngle(int ang){
  servo1.write(ang);
  angle=ang;
}
void setAngle2(int ang){
  servo2.write(ang);
  angle2=ang;
}

int getMicrosecondsFromAngle(int ang){
  return map(ang,0,180,544,2400);
}
void setAngleSlowly(int ang){
  int currentPosition=getMicrosecondsFromAngle(angle);
  int finalPosition=getMicrosecondsFromAngle(ang);
  int midPosition=(finalPosition+currentPosition)/2;
  int quarterPosition=(midPosition+currentPosition)/2;
  int threeQuartersPosition=(finalPosition+midPosition)/2;

  if(finalPosition<=currentPosition){
    for(int i=currentPosition;i>=finalPosition;i--){
        servo1.writeMicroseconds(i);
        if(i<=currentPosition && i>quarterPosition)
          delayMicroseconds(2000);
        else if(i<=quarterPosition && i>midPosition)
          delayMicroseconds(750);
        else if(i<=midPosition && i>threeQuartersPosition)
          delayMicroseconds(750);
        else if(i<=threeQuartersPosition && i>=finalPosition)
          delayMicroseconds(2000);
       }
    }
  else{
    for(int i=currentPosition;i<=finalPosition;i++){
        servo1.writeMicroseconds(i);
        if(i>=currentPosition && i<quarterPosition)
          delayMicroseconds(2000);
        else if(i>=quarterPosition && i<midPosition)
          delayMicroseconds(750);
        else if(i>=midPosition && i<threeQuartersPosition)
          delayMicroseconds(750);
        else if(i>=threeQuartersPosition && i<=finalPosition)
          delayMicroseconds(2000);
       }    
    }
  setAngle(ang);
}
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

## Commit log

2025-05-14 Adding results files. Analysis coming next.
    [Kanishk_K562_TNFA_Validation_Optical_Results - ANOVA Results.xlsx, Kanishk_K562_TNFA_Validation_Optical_Results - ANOVA Results_ANOVA.csv, Kanishk_K562_TNFA_Va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]
2025-05-14 Adding additional files in compatible formats.
    [Kanishk_K562_TNFA_Validation_Optical_Results.csv, Kanishk_K562_TNFA_Validation_Optical_Results.xlsx]
2025-05-15 Deleted unecessary file.
    [Output_Template_K562_TNFA.csv]
2025-05-21 Doing some correlation analysis. Looks good so far.
    [Selected_Genes_scK562.csv]
2025-06-24 Making updates to protocol based on current workflow.
2025-07-01 Updating Software for running chronoseq device with the ability to take cell samples from two cell reservoirs at the same time to help with qPCR exploration of THP1 inflammatory response dynamics.
2025-07-09 Reducing start_vent pressure so the gas cylinder lasts longer.
2025-07-10 Adding additional protocol for directly comparing non-adherent cells incubated inside the ChronoSeq device.
2025-07-12 Was bleeding too much gas reduced keep suspension gas flow.
2025-07-12 Adding some new information. But will need to generate more information from device directly for it to be conclusive.
    [Kanishk_K562_Costimulation_July11_2025.csv]
2025-07-23 Adding data files.
    [Kanishk_K562_Costimulation_LPS_Two_Samples.csv]
2025-07-23 Adding more info
    [Kanishk_2Sample_HPRT1_only.csv]
2025-08-13 Update to protocol. Following same temperature profile for RT similar to previous experiment. Only slightly different.
2025-10-06 Renaming for clarification.
    [Kanishk_K562_Costimulation_July11_2025.csv]
2025-10-09 Updating with latest K562 replication dataset. Values for cosine similarity are almost the same.
    [Selected_Genes_scK562.csv]
